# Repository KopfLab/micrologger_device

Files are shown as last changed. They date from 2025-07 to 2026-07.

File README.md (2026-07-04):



# *µLogger*

This repository holds the code, schematics, and documentation to build a ***M**odular **I**nternet **C**ontrollable **R**eal-time **O**ptical-density Logger* (***microLogger*** or ***µLogger*** for short). All content of this repository is free to use for noncommercial research and development efforts as outlined in the terms of the included [LICENSE file](LICENSE.md).

To cite ***µLogger*** in publications use:

> Kopf S and Younkin A, 2025. _µLogger: a Modular Internet Controllable Real-time Optical-density Logger_. <https://github.com/KopfLab/micrologger_device>

A BibTeX entry for LaTeX users is

```
@Manual{
  microLogger,
  title = {µLogger: a Modular Internet Controllable Real-time Optical-density Logger},
  author = {Sebastian Kopf and Adam Younkin},
  year = {2025},
  url = {https://github.com/KopfLab/micrologger_device}
}
```

## About

Modular Internet Controllable Real-time Optical-density Loggers (µLoggers) are optical density measurement devices for continuously recording the growth of a microbial culture directly in its culturing vessel. Each microLogger consists of a compact high strength carbon fibre culture vessel holder that has a built-in light source at a narrow band wavelength and a light sensor with automatically adjustable gain that measures the light transmission across the culture vessel to automatically and continuously quantify optical density at user defined time intervals. A magnetically coupled stirrer built into the vessel holder can agitate the culture both continuously as well as in vortexing mode  (= pulse agitation) at user-set stir/vortexing speeds from 50 to 5000 rpm. Culture vessel adapters that are magnetically secured to the vessel holder allow for quick and easy swapping for differently sized culture vessels and snugly hold the culture vessel in place using a radial spring mechanism. Adapters can be custom sized for the preferred culture vessel from standard 18mm diameter 15mL culture tubes up to 58mm GL45 100mL media bottles. Typical adapter sizes also cover culture vessels typically used in anaerobic microbial culture including balch tubes and serum bottles of varying sizes. Additional optional adapters that are magnetically secured on top of the vessel adapter can provide additional functionality such as user-controlled illumination for experiments with phototrophic microorganisms. Each µLogger is connected to a compact controller (the micrologger "brain") that connects to the culture vessel holder via a single cable such that the vessel holder can be placed inside an incubator (e.g. for temperature or gas modulation) while the controller sits outside the incubator and provides full control and power to the culture vessel holder for stirring, optical density measurements, and (optionally) lighting. The controller has built-in WiFi connectivity and receives/sends data wirelessly wirelessly. This makes it possible to monitor optical density of the microbial cultures in real-time from any location. The controller also has a built-in screen that displays the state of the micrologger (e.g. stir speed, read interval, internet connectivity) as well as the real-time data from the culture vessel so that users can check on their experiments with a glance at the controller without opening the incubator and without handling the culture vessel in any way to avoid potentially disturbing an experiment. For convenience, the controller can also be attached magnetically to the outside of the incubator (if metal) or any other metallic surface.

## Features

- **Continuous optical-density logging** — a narrow-band beam LED and an OPT101 photodetector with automatically optimized amplifier gain measure the light transmission across the culture vessel; the firmware computes optical density (−log₁₀ of transmittance) at user-defined intervals, propagates a standard-deviation error onto every reading, and stores the per-vessel zero reference on the device so it survives power outages.
- **Magnetic stirring & vortexing** — a built-in brushless motor drives a magnetically coupled stirrer with configurable speed, acceleration/deceleration ramps, and a vortex (pulse-agitation) mode; stirring can automatically pause or vortex around each optical-density read.
- **Swappable, magnetically secured vessel adapters** — 3D-printed adapters hold vessels from 18 mm / 15 mL culture tubes up to GL45 100 mL bottles (including Balch/Hungate tubes and serum bottles) with a radial spring mechanism, and accept stacking add-ons such as the illumination adapter.
- **Optional illumination for phototrophs** — a dimmable light adapter with permanent on/off or scheduled (repeating daily-cycle) operation and a light-synced cooling fan.
- **Temperature & power monitoring** — on-board TMP117 temperature sensing at the vessel holder plus supply-voltage monitoring with under-voltage warnings on the display.
- **At-a-glance local display** — the WiFi controller sits outside the incubator, links to the reader over a single cable, and shows live optical density, stir speed, temperature, connectivity, and publishing status on an OLED; it mounts magnetically to any metal surface.
- **Real-time cloud connectivity** — built on the Particle [Photon 2](https://docs.particle.io/reference/datasheets/wi-fi/photon-2-datasheet/); publishes JSON data logs via cloud webhooks (the `microloggerData` event) for recording into spreadsheets or databases, averages data over configurable intervals, and caches logs during offline periods to bridge device downtime.
- **Self-describing & remotely controllable** — the entire device state is exposed as a self-describing data structure (SDDS) that the [sddsParticle](https://github.com/KopfLab/sddsParticle) web GUI (or the Particle CLI/API) can browse and control, with persisted settings, one-shot actions, and per-variable publish intervals.
- **Open & modular** — component-based, easily extensible C++ firmware (separate `sensor`, `stirrer`, `lights`, and `environment` components), open [KiCad](https://www.kicad.org/) hardware, and open [OpenSCAD](https://openscad.org/) 3D-printable mechanical parts.

## Hardware

A µLogger is built from four custom circuit boards, designed in [KiCad](https://www.kicad.org/) with sources under [`pcbs/`](pcbs). For each board the board layout is shown below (click it to open the full schematic / wiring diagram as a PDF).

### Controller board — the µLogger "brain"

A Particle Photon 2 for WiFi and control, the OLED status display, the 24 V power input with supply-voltage monitoring, the controller-version code pins, and the single-cable connector to the reader (the vessel holder).

<a href="pcbs/controller_board/controller_board.pdf">controller board layout</a>

*→ [Controller board wiring diagram (PDF)](pcbs/controller_board/controller_board.pdf)*

### Sensor board

Mounted in the vessel holder: the OPT101 photodiode/transimpedance amplifier with a two-stage digital-potentiometer gain circuit (MCP4017 + AD5246), the TCA9534 I2C IO expander (reader-connection detection plus beam and indicator LEDs), and the measurement-beam LED. The board version is read back over the IO expander.

<a href="pcbs/sensor_board/sensor_board.pdf">sensor board layout</a>

*→ [Sensor board wiring diagram (PDF)](pcbs/sensor_board/sensor_board.pdf)*

### LED board

The optional illumination adapter: the light LEDs driven by a PCA9633 PWM controller for dimming, together with the cooling fan.

<a href="pcbs/led_board/led_board.pdf">LED board layout</a>

*→ [LED board wiring diagram (PDF)](pcbs/led_board/led_board.pdf)*

### Temperature board

A simple TMP117 precision temperature sensor placed at the vessel holder.

*→ [Temperature board wiring diagram (PDF)](pcbs/temperature_board/temperature_board.pdf)*

## 3D printed parts

The vessel holder, stirrer, controller enclosure, and all vessel adapters are 3D-printable. The STL files live in [`prints/stl/`](prints/stl) and the parametric source models are the [OpenSCAD](https://openscad.org/) files [`prints/micrologger_device.scad`](prints/micrologger_device.scad) and [`prints/micrologger_controller.scad`](prints/micrologger_controller.scad). File names ending in `_nozzle_0.4mm` are optimized for a 0.4 mm printer nozzle.

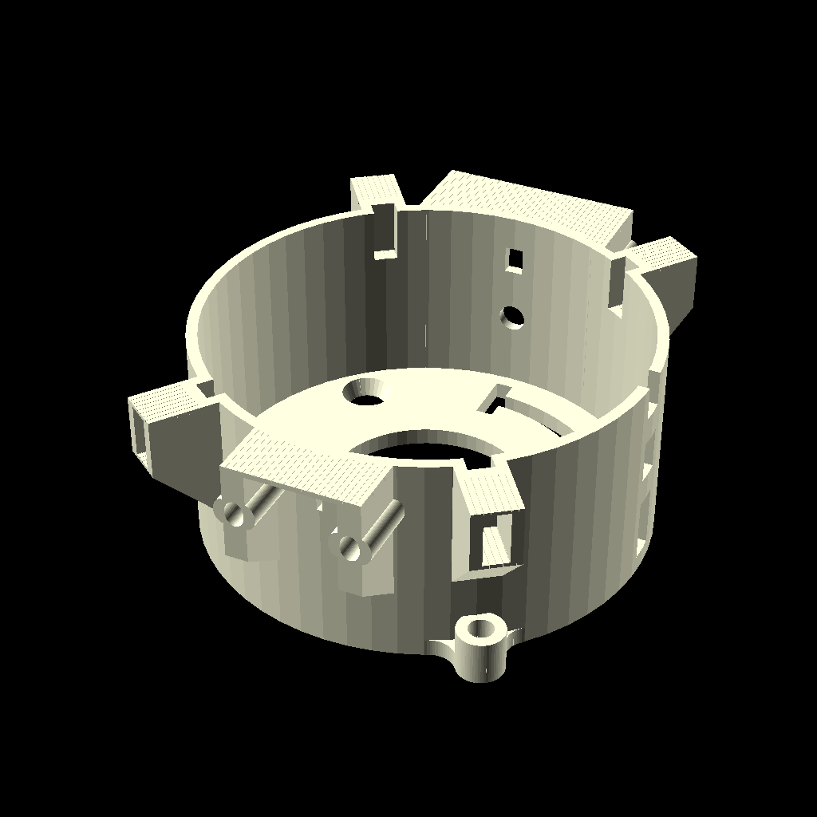
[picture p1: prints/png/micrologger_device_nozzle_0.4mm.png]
µLogger device


The parts fall into a few groups:

- **Device body & stirrer** — the high-strength vessel-holder body (`micrologger_device_*`, designed to be printed in carbon-fibre-reinforced filament) that houses the sensor/beam optics, and the magnetically coupled `micrologger_stirrer_*`.
- **Vessel adapters** — magnetically secured, radially sprung adapters sized for specific culturing vessels: `balch`, `hungate`, `culture60`, `gl45`, `serum60`/`serum120`/`serum160`, plus the `base_*` adapters that go into the base of the vessel holder for small vial sizes.
- **Light adapters** — `micrologger_light_adapter_up`/`_down` for the optional illumination add-on.
- **Controller enclosure** — `micrologger_controller_body`, `micrologger_controller_back`, and `micrologger_controller_magnet_holder` for the "brain" controller box.

👉 See [**`prints/README.md`**](prints/README.md) for the complete list of all printable parts with rendered previews.

## Building, flashing & monitoring

The firmware is written for the Particle Photon 2 (platform `p2`) and built with the [Particle Cloud command line interface (CLI)](https://github.com/spark/particle-cli). Builds are driven by Ruby [Rake](https://ruby.github.io/rake/) (see [`particle_rake.rb`](particle_rake.rb), imported by the [`Rakefile`](Rakefile)) rather than `make`.

First-time setup:

- clone this repository **with submodules** (the `lib/` libraries are git submodules): `git clone --recurse-submodules ...`, or run `git submodule update --init --recursive` in an existing clone
- install the [Particle CLI](https://github.com/spark/particle-cli) and log into your account with `particle login`
- install the ruby gems with `bundle install`

Common Rake shortcuts (run `rake help` for the full list and `rake programs` for the list of compilable programs):

- `rake micrologger` — compile the main firmware in the Particle cloud (`bin/micrologger-p2-<version>-cloud.bin`)
- `rake local micrologger` — compile locally instead (requires the [Particle Workbench](https://docs.particle.io/getting-started/developer-tools/workbench/) local toolchain installed under `~/.particle`)
- `rake dev micrologger` — local compile + flash + watch sources and auto-recompile/-flash on change (via [Guard](Guardfile))
- `rake flash` — flash the newest binary in `bin/` to a USB-connected device (must be in DFU / blinking-yellow mode)
- `rake flash DEVICE=<name>` — flash the newest binary over-the-air via the cloud
- `rake monitor` — open the USB serial monitor
- targets chain, e.g. `rake micrologger flash monitor` compiles, flashes, then monitors

The `tests/` folder holds standalone test programs that build the same way (e.g. `rake blink`, `rake motor`). Which sources/libraries each program compiles is defined in its `.github/workflows/compile-<program>.yaml` file, which drives both local `rake` builds and continuous integration.

## Communicating with the device

The µLogger firmware is built on **self-describing data structures (SDDS)** using the [SDDS library](https://github.com/mLamneck/SDDS) and the [SDDS particleSpike](https://github.com/KopfLab/SDDS_particleSpike). The entire device — every setting, action, and live reading — is exposed as a single SDDS tree (see [The SDDS structure tree](#the-sdds-structure-tree) below).

The primary way to view and control a µLogger is the web-based [sddsParticle](https://github.com/KopfLab/sddsParticle) GUI, which reads a device's structure tree and automatically builds an editor for it. You can also interact with a device directly via the [Particle CLI](https://github.com/spark/particle-cli) (or the equivalent [Particle Cloud API](https://docs.particle.io/reference/api/) requests). All calls require being logged in (`particle login`) and only work for devices registered to your account.

**Reading the tree** (Particle cloud variables):

- `particle get <deviceID> getSddsValues` — the current values of all SDDS variables
- `particle get <deviceID> getSdds` — the full structure tree (types + values)
- `particle get <deviceID> getSddsSystem` — just the `SYSTEM` subtree
- `particle get <deviceID> getSddsCommandLog` — the log of recently received commands

**Setting variables / issuing commands** (Particle cloud function `sdds`): assign values with a `path=value` syntax where the path uses `.` as the separator. Issue several assignments at once by separating them with spaces:

```sh
particle call <deviceID> sdds "sensor.action=zero"
particle call <deviceID> sdds "stirrer.setpoint_rpm=500 stirrer.action=start"
particle call <deviceID> sdds "lights.action=schedule"
```

The return value is `0` when all assignments succeed. For a single failed assignment it is the negated error code (e.g. `-2` when the path could not be resolved); for a batch of assignments it is a bitmask flagging which ones failed. Special codes: `-200` = empty command, `-201` = more than 31 assignments in one call.

**Pushing data to the cloud on demand** (Particle cloud functions): `sendSdds`, `sendSddsValues`, and `sendSddsState` publish the structure tree, all values, or just the saveable state, respectively. Regular data logging is published on the **`microloggerData`** cloud event and configured through the `SYSTEM` structure (see the [SDDS particleSpike documentation](https://github.com/KopfLab/SDDS_particleSpike#the-system-structure)).

## The SDDS structure tree

Every µLogger exposes its complete state as an SDDS tree. Fields can be flagged as _read-only_ (reported by the device but not meant to be edited by the user) or _saveable_ (persisted across restarts, i.e. restored on boot and re-saved with the `SYSTEM` `saveState` action). Numeric fields carry their unit as a name suffix (e.g. `_ms`, `_sec`, `_rpm`, `_V`, `_C`, `_Ohm`, `_percent`, `_ppt` for parts-per-thousand ‰, `_dt` for a date/time, `_HHMM` for a 24h clock time). Actions are one-shot triggers that automatically reset to `___` (no action) after they run.

The top level of the tree contains the `SYSTEM` structure, the `device` connection flag, the four functional components (`sensor`, `stirrer`, `lights`, `environment`), and a low-level `HARDWARE` menu.

### SYSTEM

The `SYSTEM` structure is added automatically by the SDDS particleSpike and carries the device's identity, connection status, health/vitals, persisted-state handling, and all data recording/publishing settings. It is documented in full in the [SDDS particleSpike documentation](https://github.com/KopfLab/SDDS_particleSpike#the-system-structure).

### device

- **`device`** — _read-only_ — whether the controller (the "brain") is connected to the reader (the culture vessel holder) via RJ45 cable: `connected` or `disconnected` (detected via the reader's I2C bus).

### sensor

Optical-density measurement — the core function of the µLogger.

- **`action`** — trigger a one-off measurement action:
  - `zero`: establish the OD = 0 reference for the current culture vessel (typically done once before inoculation). If `gain.automatic` is `yes`, the gain is auto-optimized first, then paused for `gain.zeroPause_ms`, then the zero is recorded. The zero is persisted so it survives power outages.
  - `beamOn`: turn the measurement beam LED permanently on (e.g. to watch the live `reading.saturation_ppt`)
  - `beamOff`: turn the measurement beam off
  - `optimizeGain`: run the automatic amplifier-gain optimization to bring the signal to `gain.target_ppt`
  - `reset`: clear the zero reference and return to idle
- **`status`** — _read-only_ — `idle`, `reading`, `optimizing`, `waiting`, or `zeroing`
- **`reading`** — the latest measurement plus read timing/behavior settings
  - **`saturation_ppt`** — _read-only_ — the current live beam signal as a fraction of the ADC maximum, in ‰; watch this to avoid saturating the detector
  - **`readInterval_ms`** — _saveable_ — how often to take an OD reading (default: 2 minutes)
  - **`vortex`** — _saveable_ — vortex (pulse-agitate) the culture before each read (default: no)
  - **`stopStirrer`** — _saveable_ — stop the stirrer before each read (default: yes)
  - **`stopLights`** — _saveable_ — turn the light off during each read (default: yes)
  - **`wait_ms`** — _saveable_ — settling time after vortex/stirrer stop before reading (default: 0)
  - **`warmup_ms`** — _saveable_ — beam warm-up time whenever the beam turns on (default: 3000)
  - **`cooldown_ms`** — _saveable_ — wait after the beam turns off before reading the dark background (default: 500)
  - **`nextRead`** — _read-only_ — human-readable countdown to the next read
  - **`signal`** / **`signalSd`** — _read-only_ — mean and standard deviation of the beam (lit) signal of the last read
  - **`bgrd`** / **`bgrdSd`** — _read-only_ — mean and standard deviation of the dark-background signal of the last read
  - **`transmittance`** / **`transmittanceSd`** — _read-only_ — light transmittance relative to the zero reference, and its error
  - **`OD`** / **`ODSd`** — _read-only_ — optical density (−log₁₀ of transmittance) and its error
- **`zero`** — the zero reference, persisted so it survives power outages
  - **`last_dt`** — _read-only, saveable_ — timestamp of the last zeroing (`never` if never zeroed)
  - **`valid`** — _read-only, saveable_ — whether a valid zero exists; OD is only computed once this is `yes`
  - **`signal`** / **`signalSd`** — _read-only, saveable_ — beam signal (and SD) recorded at zeroing
  - **`bgrd`** / **`bgrdSd`** — _read-only, saveable_ — dark background (and SD) recorded at zeroing
- **`beam`** — the measurement-beam LED
  - **`status`** — _read-only_ — `on`, `off`, or `error`
  - **`error`** — _read-only_ — I2C error of the beam control
- **`gain`** — the signal amplifier gain
  - **`automatic`** — auto-optimize the gain before zeroing (default: yes; not persisted, so it must be re-enabled each session)
  - **`zeroPause_ms`** — _saveable_ — settling pause after automatic gain optimization before zeroing (default: 60000)
  - **`max_ppt`** — _read-only_ — the maximum attainable signal, in ‰
  - **`target_ppt`** — _saveable_ — target signal level for gain optimization, in ‰ (default: 920)
  - **`gain_Ohm`** — _read-only, saveable_ — the current total amplifier resistance (i.e. the gain), persisted across restarts
  - **`status`** — _read-only_ — `set` or `error`
  - **`error`** — _read-only_ — I2C error of the gain control
- **`error`** — _read-only_ — top-level OD error: `none`, `saturated`, `failedGain`, `failedZero`, or `failedRead`

### stirrer

The magnetically coupled stirrer built into the vessel holder.

- **`action`** — trigger a one-off stirrer action:
  - `start` / `stop`: turn continuous stirring on/off (also updates the persisted `state`)
  - `pause` / `resume`: temporarily stop/restart the motor **without** changing `state` (used internally during reads)
  - `vortex`: run a single vortex pulse — ramp up to `settings.vortexSpeed_rpm`, hold for `settings.vortexTime_sec`, then return to the previous speed
- **`state`** — _read-only, saveable_ — the persisted on/off intent of the stirrer (default: off)
- **`status`** — _read-only_ — `off`, `accelerating`, `decelerating`, `running`, or `error`
- **`error`** — _read-only_ — motor error
- **`event`** — _read-only_ — transient activity: `none`, `paused`, or `vortexing`
- **`setpoint_rpm`** — _saveable_ — target stir speed in rpm (default: 500)
- **`speed_rpm`** — _read-only_ — the measured actual speed in rpm
- **`settings`**
  - **`acceleration_rpm_s`** — _saveable_ — acceleration ramp in rpm per second (default: 500)
  - **`deceleration_rpm_s`** — _saveable_ — deceleration ramp in rpm per second (default: 3000)
  - **`maxSpeed_rpm`** — _saveable_ — maximum allowed speed (capped by the motor hardware limit)
  - **`vortexSpeed_rpm`** — _saveable_ — the speed of a vortex pulse (default: 3000)
  - **`vortexTime_sec`** — _saveable_ — how long to hold at vortex speed (default: 2)

### lights

The optional illumination adapter (for experiments with phototrophic microorganisms) and its cooling fan.

- **`action`** — trigger a one-off light action:
  - `on` / `off`: turn the light permanently on/off
  - `schedule`: run the light on a repeating on/off schedule (see the `schedule*` settings below)
  - `pause` / `resume`: temporarily turn the light off/back on without changing `state` (used during reads when `sensor.reading.stopLights` is yes)
- **`state`** — _read-only, saveable_ — the persisted light mode: `on`, `off`, or `schedule` (default: off)
- **`status`** — _read-only_ — the actual light output: `on`, `off`, or `error`
- **`event`** — _read-only_ — `none` or `paused`
- **`error`** — _read-only_ — I2C error of the light/fan driver
- **`intensity_percent`** — _saveable_ — light brightness, 1–100% (default: 100)
- **`scheduleOn_sec`** — _saveable_ — how long the light stays on per schedule cycle (default: 12 hours)
- **`scheduleOff_sec`** — _saveable_ — how long the light stays off per schedule cycle (default: 12 hours)
- **`scheduleOnStart_HHMM`** — _saveable_ — the time of day the on-phase begins, as a 24h `HHMM` value (default: 1200 = noon)
- **`scheduleInfo`** — _read-only_ — human-readable countdown to the next on/off switch
- **`fan`** — the cooling fan for the light adapter
  - **`action`** — `on`, `off`, or `withLight`
  - **`state`** — _read-only, saveable_ — the persisted fan mode: `on`, `off`, or `withLight` (run the fan only while the light is on) (default: withLight)
  - **`status`** — _read-only_ — `on`, `off`, or `error`

### environment

Temperature and supply-power monitoring.

- **`readInterval_ms`** — _saveable_ — how often to read the temperature sensor (default: 1000)
- **`temperature_C`** — _read-only_ — temperature measured at the vessel holder, in °C
- **`power_V`** — _read-only_ — supply voltage measured at the controller, in V
- **`powerReq_V`** — _saveable_ — the minimum required supply voltage; below this the display warns "not enough power" (default: 20.0)
- **`error`** — _read-only_ — I2C error of the temperature sensor

### HARDWARE

An advanced, low-level menu (added at the end of the tree) that exposes direct access to every peripheral — the I2C IO expander, the digital potentiometers and amplifier gain circuit, the OPT101 light sensor, the TMP117 temperature sensor, the supply-voltage divider, the PCA9633 light/fan PWM driver, the Nidec motor, the OLED display, and the detected controller/sensor PCB versions. It is intended for diagnostics and calibration only; the `sensor`, `stirrer`, `lights`, and `environment` components above are the normal interface.

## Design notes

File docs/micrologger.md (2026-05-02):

# this is basically the ministat v2

# sensor - OPT101

## power

- can run at any voltage from 2.7 to 36V and output is **indepenent** of the input voltage but will max out ~1V below the power and no longer record higher light intensities
- to max out GPIO input (3.3V), need to drive at > 4V (5V works well) but then need to also protect the GPIO input against overvoltage which gets problematic at ~3.7 V
- to protect this, use a small signal schottky diode with low forward voltage drop (ideally ~200mV) to the 3.3V supply to clamp the voltage on the GPIO pin to 3.3V + 0.2V = ~ 3.5 V, options:
    - BAT41: at 1mA max drop is 450mV (looks like ~250mV at 0.1mA) and very low leakage current (only 100 nA at 50V) --> seems to have the lowest leak A and V drop for through hole components
    - BAT43W (SMD only): at 2mA max drop is 330mV, 450mV at 15mA
    - BAT54 (SMD only): at 0.1mA max drop is 240mV, 1mA max drop is 320mV (very similar to 43W)
    - BAT81, 82, 83: at 0.1mA max drop is 330 mV    
    - some other options: https://www.vishay.com/en/diodes/ss-schottky/

## I2C addresses:

 - MCP4652 (dual trimpot): 0x2C if address pins tied to ground
 - MCP5241 (single trimpot): 0x2C if address pins tied to ground
 - I2C display: 0x3c
 - IR temperature sensor: 0x5a
 - tmp117 temperature sensor: 0x48
 - TCA9534 gpio expander: 0x20 --> https://learn.sparkfun.com/tutorials/sparkfun-qwiic-gpio-hookup-guide#arduino-examples
 - PWM controller PCA9633: 0x62 for inidviual, 0x70 for AllCall address (to all PCA9633 chips), and 0x03 for software reset. This chips is a 4-bit, 4 channel fan (mosfet), light sheet (mosfet)
 - not used MCP4017: 0x2f --> https://github.com/SparkysWidgets/SW_MCP4017-Library
 - not used AD5246: 0x2e --> https://github.com/SparkysWidgets/SW_MCP4017-Library

## signal

- typically need to reduce the signal amplification with resistors < 1MOhm
- with LED driven at ~3.3V from a GPIO pin, a ~250 kOhm resistor usually maxes out the detector to its reference voltage even if it's as high as 24V
- the current is typically low, even at full intensity with a high resistor value (and corresponding signal voltage), this stays < 10µA (but will rise rapidly if it exceeds the internal GPIO overvoltage of ~3.7V) - for stability best to stay at max overvolage of 3.4V (not all the way to 3.7!), this can be reached with a supply voltage of 4.2V to the OPT100 and light saturation --> a voltage divider with 1kOhm and 6.8kOhm will lead to voltage of ~4.2V (starting with 5V supply, note that voltage divider predicts slightly higher but we have some pulls to GND that lower this slightly) which should work for this. Current draw of the opt can be up to 4mA current to OPT101 (and ~0.7mA dead current from source to sink)
- if signal instability is an issue, can place a 0.01-μF to 0.1-μF (e.g. 67 pF) bypass capacitor close to sensor to connect Vin & Gnd. Additionally for low resistanece (i.e. low amplification) at or below 100 kOhm, might also need a capacitor (33 pF for 100kOhm, higher for others) across the resistor
- pulldown resistor to signal line should be 10 kOhm or bigger (no need to have them lower since the voltage is clamped to ~3.7V), use 47 kOhm or even 100 kOhm as a more common pulldown! Note that using an external resistor is a bit more reliable than internal (digital) pulldowns which are different on different pins and from controller to controller - this resistor could be surface mounted
- a digital trimmer could provide programmatic control over the amplification, try out AD5241 (1 trimmer with 2 additional logic outputs), which could also logic control 2 other things via the I2C (e.g. motor on/off, and with a MOSFET the LED on/off) --> since the AD5241 runs 5V logic, need to use a level shifter for Argons/P2s, simplest is this tiny Pololu PCB with mosfets (https://www.pololu.com/product/2595) or slightly bigger Sparkfun PCB with BSS138 mosfets (probably works too with BS270): https://cdn.sparkfun.com/datasheets/BreakoutBoards/Logic_Level_Bidirectional.pdf - alternatively just make the level shifting circuits yourself on the controller PCB

# amplification / digital potentiometer

need to be able to cover a range of ~200 kOhm but the most commonly available are 100 kOhm (1 MOhm could work too but then the gain adjustment is too course), this is achieved most easily by a either a dual 100kΩ rheostat or two separate 100kΩ rheostats

## 1 dual rheostat

 - MCP4652 100kΩ Dual Rheostat, tempco 50 ppm/C, 8-bit (256 steps): https://jlcpcb.com/partdetail/MicrochipTech-MCP4652T_104EMF/C623638
 - alternative (with 2 extra pins): MCP4651 100kΩ Dual Potentiometer version of MCP4652 https://jlcpcb.com/partdetail/MicrochipTech-MCP4651_104EST/C637129
 - AD5248 is the equivalent to MCP4652 (8-bit 100kΩ Dual Rheostat) but only 35 ppm/C tempco, also a lot more expensive and not as available: https://jlcpcb.com/partdetail/AnalogDevices-AD5248BRMZ100/C144252, this might be useful for programming: https://learn.adafruit.com/ds3502-i2c-potentiometer/overview

## 2 single rheostats

 - AD5246 100kΩ Single Rheostat, tempco 45ppm/C, 4-bit (128 steps): https://jlcpcb.com/partdetail/AnalogDevices-AD5246BKSZ100RL7/C649406
 - MCP4017 100kΩ Single Rheostat, tempco 50ppm/C, 4-bit (128 steps): https://jlcpcb.com/partdetail/MicrochipTech-MCP4017T_104ELT/C510890 (discontinued)
 - newer version: MCP40D17 (same specs as MCP4017): https://jlcpcb.com/partdetail/MicrochipTech-MCP40D17T_104ELT/C115214 (not available yet)
 - MCP4532 100kΩ Single Potentiometer, tempco 50ppm/C, 4-bit (128 steps): https://jlcpcb.com/partdetail/MicrochipTech-MCP4532T_104EMS/C627275

# LED - 630nm (MTE7063NK2)

 - this LED has 50mA max current but best to drive at 20-30mA where it has ~1.9 V forward voltage
 - with 47 Ohm resistor and 3.3V supply this runs at ~30mA
 - with 100 Ohm resistor and 5V supply this runs at ~31mA  
 - can drive the LED from the AD5241 extra logic output with a BS170 or BS270 (lower gate voltage?) mosfet (or the equivalent SMD component) --> keep in mind that as diodes these have forward voltage drops that will aslo affect the LED current! need to test this out but it should only be a few mV

# temperature sensing

 - use a temp sensor via I2C since that's already going to the micrologger now
 - ideally use tmp117 (https://cdn.sparkfun.com/assets/2/0/f/c/a/SparkFun_TMP117_Qwiic_Schematic_v1.pdf, address 0x48) but I don't see a good packaged version yet, alternatively the tmp100? another interesting option is a low angle (10degree) IR temperature sensor, such as this one: https://www.digikey.com/en/products/detail/melexis-technologies-nv/MLX90614ESF-ACF-000-TU/2652200 that can communicate via I2C like protocol, this one could go right underneat the light sensor on the same PCB and going through the wall of the micrologger (it's okay if it records IR from the stir bar + liquid) - for notes on how to get started with communication, check out this testing board: https://www.sparkfun.com/products/10740

# display

 - switching to oled: https://www.youtube.com/watch?v=7x1P80X1V3E with this model (which is easily available from various amazon vendors for about $14): https://www.amazon.com/gp/product/B09LND6QJ1
 - needs to be switched from SPI to I2C
 - great resource: https://luma-oled.readthedocs.io/en/latest/hardware.html
 - great summary of the different resistors: https://www.amazon.com/gp/customer-reviews/R373WMLIYUB5MF/ref=cm_cr_dp_d_rvw_ttl?ie=UTF8&ASIN=B09LND6QJ1
 - attach to PCB with M2.5 x 28mm threaded spacers from Mouser (761-M1273-2545-AL) and with narrow head M2.5 x 6mm machine screws from McMaster (cheaper: 91800A126 or nicer: 94017A152)
 - don't want to have it on the 3.3V so we don't have any interference but also a problem if it's on the 5V when the 5V rail is competing between the USB and DC/DC adapter

# lights

 - Auragami light sheets need 24V power and are 26mW (~1.1 mA at 24V) per LED --> with 40 LEDs this should only be about 50mA

# motor

 - Nidec 24H brushless servo motor requires 22.8 to 25.2V to power. No-load current at 24V (5200 to 6400rpm) is about 110mA, max power is 11W (~460mA)
    -> pin 8/red: power (+24VDC)
    -> pin 7/black: ground (GND)
    -> pin 6/yellow: speed (as long as break is not engaged), freq 20 to 30 kHz (25000 works welll), duty cycle = speed (0 = stop, 255 = max speed)
      note: LED dimmers like the PCA9633 we're using cannot operate at this frequency, the simplest solution if we do not want to use a line on the RJ45 for motor speed is to use a small microcontroller (e.g. ATtiny402) on the sensor board side that talks to the photon by I2C and takes care of the PWM for the motor, the LED on/off and the light control
    -> pin 5/green: break, HIGH = engaged (stop), LOW = not engaged (pin 6 decides speed) --> set permanently to LOW
    -> pin 4/blue: direction, HIGH (2 to 5V) = CW, LOW = CC --> set permanently to one or the other (jumper selectable?)
    -> pin 3/white: power for the decoder, can be 5 VDC or 3.3 VDC --> pin 7/8 signals are this voltage use 3.3 VDC OR use a level shifter (can use multiple channel ones, one for the I2C, one for this?)
    -> pin 2/orange: signal of the optical decoder, seems like it has 100 pulses per revolution so freq (in Hz) / 100 * 60 = rpm
    -> pin 1/brown: offset (falling edge) of the decoder, same info as pin 2 if we already know cc vs cw
        - 0/255: stop
        - 1/255: doesn't work
        - 2/255: 37 Hz ~ 22 rpm
        - 3/255: 78 Hz ~ 47 rpm
        - 4/255: 116 Hz ~ 70 rpm
        - 5/255: 153 Hz ~ 92 rpm
        - 10/255: 330 Hz ~ 198 rpm
        - 20/255: 694 Hz ~ 416 rpm
        - 50/255: 1.6 kHz ~ 960 rpm ~ 50 mA without load
        - 100/255: 3.1 kHz ~ 1860 rpm ~ 140 mA without load
        - 150/255: 4.9 kHZ ~ 2900 rpm ~ 170 mA without load
        - 255/255: 9.54 kHz ~ 5700 rpm ~ 70 mA without load (current max without load actually seems to be around 150/255)
        --> estimated formula for 8 bit: x/255 --> rpm = (x-1) * 22 rpm (response factor more like 20rpm around 150/255 and then goes back to 22 rpm again)
        --> for 12 bit:
        --> x = (rpm/22 + 1) * 16 = 16 + rpm * 16/22
        - with interrupt delays of about 40-70uS we should be able to measure the entire range (10 kHz = 100µs interrupts) but I'm not sure if anything else will mess with that during operation

## motor power

 - the speed pin (6/yellow) needs to be pulled low to GND otherwise the motor spins on start-up (unless break is engaged which can cause other problems)
    --> if pulled low with 1kOhm resistor the voltage is about 0.44V (see analysis below) which suggests the motor has an internal pullup on this pin to 5V of about ~10 kOhm
    --> if controlling this with a mosfet, need to provide an alternative path to high voltage that pulls the voltage above ~0.7V (also considering the body diode voltage drop of the moseft, ~0.8V at most)
    --> see circuit analysis
 - resistor values for pull down to ground (assumes ON = direct connection to 5V):
    - 2.3kOhm: pull down does NOT work because effective voltage on the pin is 1.34V (counts as HIGH), 0.35 mA to GND
    - 2.2k: 0.845 V, 0.4 mA to GND when off, 2.2mA to GND when on
    - 1.5k: 0.597 V, 0.42 mA to GND when off, 3.34mA to GND when on (2mA if 3.3V supply voltage)
    - 1k: 0V, 0.44 mA to GND when off, 5mA to GND when on (3mA if 3.3V supply voltage)
 --> with a BSS138 use a 1000 Ohm resistor to pull to ground (with the 10kOhm pull up internally to 5V, this gives a voltage of 0.44V which is low enough to deactivate the motor and only a 0.5mA standby current)
 --> then the mosfet shifts it with a parallel resistor to 5V that is 1kOhm which makes the net resistor 900 Ohm and pulls the voltage to ~2.5V which is enough to activate motor and a total of ~2.6 mA current which is totally fine
 --> I modeled this in a circuit lab circuit (but don't have good access)
 Note that this circuit is divided between the sensor board (with the pulldown to GND to have it off by default), and the brain where the I/O step up from 3.3 V to 5V is located (unidirectional level shifter if you will) mostly beccause space is abundant on this end but really limited on the sensor board but in theory this could all be sitting on the sensor board side

## motor attachment

corner standoffs for micrologger base
- base is 34 mm high
- rotor is 20 mm above base
- magnet holder is at least 3.5 mm tall (3.2 mm magnets plus 0.25mm base layer)
- i.e. total is 57.5mm
- with the longest metric standoffs from McMaster (52mm long, 95947A087) this requires a rather thick base (>5.5mm) so need to go with an imperial standoff: 2.25" is 57.15mm long (93505A006) which is male/female and thus can just thread directly into the nylon base

mounting standoffs for motor itself
- base plus mounting bracket is 3.5 mm above the motor base so 20mm shaft + 3.5 mm magnet holder - 3.5mm bracket height  - 4mm µlogger base thickness = 16mm M4 standoffs (McMaster, 95947A050). For a little extra clearance might have to make the base 5mm thick!
- plus 6mm round head M4 screws (92000A216) to attach from motor side, and 10mm flat head M4 screws (92010A220) to attach through µLogger base

## motor magnets
- 3.2 mm above the motor shaft, design/print upside down with a thin layer (0.25 mm) base then the magnet holes above (unroofed since the top of the motor assembly will hold them in place) and then the side walls above where there is solid support underneath to grip the motor shaft with the teeth walls --> total is ~3.5 mmm above the motor shaft so total then becomes 54mm + 3.5mm = 57.5mm which requires a rather thick base (~5.5mm to still work with the 52mm feet)
-  

# overall power

power over ethernet technical specs (up to 100m distance): https://www.blackbox.com/en-nz/insights/blogs/detail/technology/2021/05/04/poe-cabling-what-you-need-to-know-part-1
 - PoE+	IEEE 802.3at (Type-2)	25.5 W	30 W	2-pair	0.6 A	PTZ cameras, video IP phones, alarm systems
 - PoE++ IEEE 802.3bt (Type 4)	71.3 W	100 W	4-pair	0.96 A	PoE-Powered LED Lighting, outdoor PTZ cameras

but technical specs:
    Maximum Current Carrying Capacity of Ribbon Cable (while keeping temperature rise to less than 30 °C)
    24 AWG	3.0 A
    26 AWG	1.8 A
    28 AWG	1.5 A
    30 AWG	1.1 A

# power supply voltage

 - R1: 10kOhm = 9.93
 - R2: 200kOhm = 200.1

forward voltage drop across the M400x diode is 0.6 V with minimal current and ~0.9 V at 1A (probably best to calculate with assumed 0.9V drop)

sensing calculation:
V at A0 = Vin * R1/(R1+R2) --> Vin = A0 * (10 + 200)/10 + 0.9V

 External voltage sensing on P2 pin A0:
  - R1 = 150 kOhm, R2 = 10 kOhm
  --> V at A0 for 24V --> 24V * 10/(10+150) = 1.5External voltage sensing on P2 pin A0:
   - R1 = 150 kOhm, R2 = 10 kOhm
   --> V at A0 for 24V --> 24V * 10/(10+150) = 1.550

# ethernet cable

 - 8p8c: 1=Gnd, 2=24V, 3=I2C-SDA, 4=I2C-SCL, 5=Motor-speed, 6=Detector-signal, 7=Light-intensity, 8=Motor-decoder
 -> 24V to 5V required on distribution board; level shifters required to convert 5V from I2C and motor-decoder

# connectors

 - the JST XHP connectors (2.54mm) are used by the light sheets and are easy to buy from amazon, including different length cables that can be easily assembled
 - the JST PH (2.0mm) connectors are primarly used to connect batteries (e.g poli) and usually are male to female connectors
 - the JST ZH connectors (1.5mm, 26 AWG, 1.0 A rating), are used by the motor connectors / JST ZR connectors are compatible but lower amperage rating (0.7A, 28 AWG)

# housing
 - threaded spacers between OLED and main PCB are M2.5, 28mm long: https://www.mouser.com/ProductDetail/761-M1273-2545-AL
 - standoff spacers between main PCB and back wall are M3, 12mm long (this length does not seem to be available for M2.5): https://www.mcmaster.com/94669A307/

# checklist

 - power up with 24V / GND pins (not via ethernet!)
 - when powered up but beam OFF:
    - signal vs. gain resistance should be ~200kOhm (100 kOhm base resistor + 2 * 50 kOhm = midpoints of the digipots), doesn't matter if motor and/or light are also on
    - when a little bit of light is shining on the detector, the resistance should go up (with much light into several MOhm and too high to measure)
    - signal vs. ground voltage should be < 20mV, when detector opening completely covered ~ 10mV (this is a bit higher with motor and/or lights on and/or beam on but detector covered up)
    - when a little bit of light is shining on the detector, the voltage should go up
 - when powered up and beam ON:
    - signal vs gain restiance should be immesurably high (unless detector is covered in which case it should be back to ~200 kOhm)
    - signal vs ground voltage should be at ~3.2 V
 - plugging in the ethernet cable should only have minimal effects (both loose cable and connector to empty/microcontroller less brain)
 - neither should switching to brain powersupply have any effect

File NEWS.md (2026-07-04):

NB:
 - version updates at the 0.x level usually require a state reset because they change/add/remove state variables, i.e. should never be done in the middle of an experiment. 
 - version changes at the 0.0.x level can be flashed at any time. They do make state changes and thus will resume their current state correctly after flash+restart.

# version 1.5.1

- publish on the `microloggerData` event instead of `sddsData` for microloggers
- rename `publishing.publish` to `publishing.record` to clarify how it relates to GUI recording on/off
- hardware `signal.calculation` added with two possible values: `mean` (default, average signal values) or `mode` (determine peak of the signal values)
- optical density `reading.stopLights` added for users to decide whether lights turn off or stay on during OD reads (default is stopLights = yes)
- system `state.autoSendOnStartup` added for users to decide whether to send the state snapshot whenenver a device that's recording starts up (e.g. after power cycling), default is ON
- introduce particle variable `getSddsSystem` as convenience access piont that returns the system variable tree only (~800 bytes in size) except for the variable publish intervals (which can be any size)
- change default read interavl to 2 min and default publish interval to 20 min

# version 1.4.0

- `cooldown` (wait time until dark measurement after LED beam turned off, default: 500 ms) added - this value is saved in the micrologger state
- `zeroPause` (wait time until zeroing when automatic gain adjustment happens during zeroing, default: 60s) introduced - this value is saved in the micrologger state
- default values for `warmup` (default: 3s) and `wait` (default: 0s) adjusted since the longer warmup leads to a more stable signal but usually does not require additional wait time anymore for the culture to settle

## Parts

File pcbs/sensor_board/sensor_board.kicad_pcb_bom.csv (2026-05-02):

Designator | Quantity | Value | Footprint | Package | MPN | DNP | Mount_Type | Description | JLCPCB | JLCPCBURL | DigiKey | DigiKeyURL
C1 | 1 | 100pF | C_0603 |  |  |  | smt | Unpolarized capacitor | C14858 | https://jlcpcb.com/partdetail/15530-CL10C101JB8NNNC/C14858
C2, C3, C4, C5 | 4 | 100nF | C_0603 |  |  |  | smt | Unpolarized capacitor | C1591 | https://jlcpcb.com/partdetail/1943-CL10B104KB8NNNC/C1591
D1 | 1 | Red 631nm 2.0V | LED_1206 |  | LTST-C150KRKT |  | smt | Red 631nm LED Indication - Discrete 2V 1206 (3216 Metric) | C125086 | https://jlcpcb.com/partdetail/LiteOn-LTSTC150KRKT/C125086 | 160-1405-1-ND | https://www.digikey.com/en/products/detail/liteon/LTST-C150KRKT/386761
D2 | 1 | Yellow 571nm 2.0V | LED_1206 |  | LTST-C150KGKT |  | smt | Green 571nm LED Indication - Discrete 2V 1206 (3216 Metric) | C125085 | https://jlcpcb.com/partdetail/LiteOn-LTSTC150KGKT/C125085 | 160-1404-1-ND | https://www.digikey.com/en/products/detail/liteon/LTST-C150KGKT/365085
D3 | 1 | 1A/40V/500mV | D_DO-214AC_SMA |  | SS14 |  | smt | Diode 40 V 1A Surface Mount DO-214AC (SMA) | C83852 | https://jlcpcb.com/partdetail/onsemi-SS14/C83852 | SS14CT-ND | https://www.digikey.com/en/products/detail/onsemi/SS14/965474
J1 | 1 | 1.5mm | JST_ZH_2POS_RA |  | S2B-ZR |  | tht | Connector Header Through Hole, Right Angle 2 position 0.059" (1.50mm) |  |  | 455-1669-ND | https://www.digikey.com/en/products/detail/jst-sales-america-inc/S2B-ZR/926576
J2, J3 | 2 | 2.5mm | JST_XH_2POS_RA |  | S2B-XH-A |  | tht | Connector Header Through Hole, Right Angle 2 position 0.098" (2.50mm) |  |  | 455-S2B-XH-A-ND | https://www.digikey.com/en/products/detail/jst-sales-america-inc/S2B-XH-A/1651055
J4 | 1 | 1.5 mm | JST_ZR_8POS_RA |  | S8B-ZR |  | tht | Connector Header Through Hole, Right Angle 8 position 0.059" (1.50mm) |  |  | 455-S8B-ZR-ND | https://www.digikey.com/en/products/detail/jst-sales-america-inc/S8B-ZR/926582
J5 | 1 | RJ45 | RJ45_A-2014-2-4-N-T-R |  | A-2014-2-4-N-T-R |  | tht | Jack Modular Connector 8p8c (RJ45, Ethernet) Vertical Unshielded |  |  | AE10396-ND | https://www.digikey.com/en/products/detail/assmann-wsw-components/A-2014-2-4-N-T-R/2183647
J6 | 1 | Conn_01x06 | PIN_HEADERS_1X06 |  |  |  | tht | Basic 0.1" PTH
J7, J8 | 2 | Conn_01x02 | PIN_HEADERS_1X02 |  |  |  | tht | Basic 0.1" PTH
JP1, JP2, JP3, JP4 | 4 | ~ | Jumper_3_NC-1_Trace |  |  |  | tht | 3-pole Solder Jumper, pins 1+2 closed/bridged
Q1, Q2, Q3 | 3 | 220mA / 50V | SOT-23-3 |  | BSS138 |  | tht | N-Channel 50 V 2200mA 350mW (Ta) Surface Mount SOT-23-3 | C52895 | https://jlcpcb.com/partdetail/onsemi-BSS138/C52895 | BSS138CT-ND | https://www.digikey.com/en/products/detail/onsemi/BSS138/244210
R1, R11, R3, R5 | 4 | 1kΩ | R_0603 |  |  |  | smt | Resistor, US symbol | C118155 | https://jlcpcb.com/partdetail/PANASONIC-ERJ3EKF1001V/C118155
R10, R15, R9 | 3 | 150Ω | R_0603 |  |  |  | smt | Resistor, US symbol | C400650 | https://jlcpcb.com/partdetail/PANASONIC-ERJ3EKF1500V/C400650
R12, R13, R14, R16, R2, R7, R8 | 7 | 10kΩ | R_0603 |  |  |  | smt | Resistor, US symbol | C191124 | https://jlcpcb.com/partdetail/PANASONIC-ERJ3EKF1002V/C191124?_t=1765754579496
R4 | 1 | 10kΩ | R_1206 |  |  |  | smt | Resistor, US symbol | C17902 | https://jlcpcb.com/partdetail/18590-1206W4F1002T5E/C17902
R6 | 1 | 5.6kΩ | R_0603 |  |  |  | smt | Resistor, US symbol | C403276 | https://jlcpcb.com/partdetail/PANASONIC-ERJ3EKF5601V/C403276
S1 | 1 | Value | OPT101 |  | OPT101 |  | tht | Optical Sensor Ambient 650nm Voltage 8-DIP (0.300", 7.62mm) |  |  | 296-23090-5-ND | https://www.digikey.com/en/products/detail/texas-instruments/OPT101P/251177
S2 | 1 | IR temp sensor, -40°C to +85°C | MLX90614 |  | MLX90614ESF-ACC-000-TU |  | tht | Temperature Sensor Digital, Infrared (IR) -40°C ~ 85°C 16 b TO-39, 5V |  |  | MLX90614ESF-ACC-000-TU-ND | https://www.digikey.com/en/products/detail/melexis-technologies-nv/MLX90614ESF-ACC-000-TU/1948826
U1 | 1 | 8-28V in / 5V 5W out | DC_DC_converter_R-78E5.0-1.0 |  | R-78E5.0-1.0 |  | tht | Linear Regulator Replacement DC DC Converter 1 Output 5V 1A 8V - 28V Input |  |  | 945-2201-ND | https://www.digikey.com/en/products/detail/recom-power/R-78E5-0-1-0/4930585
U2 | 1 | 8x GPIO | SOT-403-1_TSSOP16 |  | TCA9534PWR |  | tht | I/O Expander 8 I2C 400 kHz 16-TSSOP | C783615 | https://jlcpcb.com/partdetail/TexasInstruments-TCA9534PWR/C783615 | 296-40574-1-ND | https://www.digikey.com/en/products/detail/texas-instruments/TCA9534PWR/5004966
U3 | 1 | 4x PWM | SOT-505-1_TSSOP8 |  | PCA9633DP1,118 |  | smt | LED Driver IC 4 Output Power Switch I2C Dimming 25mA 8-TSSOP | C88381 | https://jlcpcb.com/partdetail/NXPSemicon-PCA9633DP1118/C88381?_t=1765688339929 | 568-3236-1-ND | https://www.digikey.com/en/products/detail/nxp-usa-inc/PCA9633DP1-118/1033521
U4 | 1 | 1 MOhm | 14-SOIC |  | AD5241BRZ1M |  | smt | Digital Potentiometer 1M Ohm 1 Circuit 256 Taps I2C Interface 14-SOIC | C649389 | https://jlcpcb.com/partdetail/AnalogDevices-AD5241BRZ1M/C649389 | 505-AD5241BRZ1M-ND | https://www.digikey.com/en/products/detail/analog-devices-inc/AD5241BRZ1M/617299
U5 | 1 | 100 kOhm | SOT-363_TSSOP6_SC88 |  | MCP4017T-104E/LTY |  | smt | Digital Potentiometer 100k Ohm 1 Circuit 128 Taps I2C Interface SC-70-6 | C510890 | https://jlcpcb.com/partdetail/MicrochipTech-MCP4017T_104ELT/C510890 | 150-MCP4017T-104E/LTYCT-ND | https://www.digikey.com/en/products/detail/microchip-technology/MCP4017T-104E-LTY/26812128

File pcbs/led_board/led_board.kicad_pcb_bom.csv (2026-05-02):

Designator | Quantity | Value | Footprint | Package | MPN | DNP | Mount_Type | Description | DigiKey | DigiKeyURL | Sim.Pins | URL | JLCPCB | JLCPCBURL | FP_Status
J1 | 1 | CONN HEADER R/A 2POS 1.5MM | JST_ZH_2POS_RA |  | S2B-ZR |  | tht | Connector Header Through Hole, Right Angle 2 position 0.059" (1.50mm) | 455-1669-ND | https://www.digikey.com/en/products/detail/jst-sales-america-inc/S2B-ZR/926576
LED1 | 1 | 630nm 1.9V 50mA | TO-46-2 |  | MTE7063NK2-UR |  | tht | Visible Emitter 630nm 1.9V 50mA 5° TO-46-2 Lens Top Metal Can | 1125-1382-ND | https://www.digikey.com/en/products/detail/marktech-optoelectronics/MTE7063NK2-UR/6817919 | 1=K 2=A | https://www.digikey.com/en/products/detail/marktech-optoelectronics/MTE7063NK2-UR/6817919
R1 | 1 | 22Ω | R_1206 |  |  |  | smt | Resistor, US symbol |  |  |  |  | C17958 | https://jlcpcb.com/partdetail/18646-1206W4F220JT5E/C17958
R2 | 1 | 56Ω | R_1206 |  |  |  | smt | Resistor, US symbol |  |  |  |  | C17995 | https://jlcpcb.com/partdetail/18683-1206W4F560JT5E/C17995 | done
U1 | 1 | 1.4-40V PWM Dimmer 100mA | SOT-23-6 |  | BCR401UW6Q-7 |  | tht | LED Driver IC 1 Output Linear PWM Dimming 100mA SOT-26 | BCR401UW6Q-7DICT-ND | https://www.digikey.com/en/products/detail/diodes-incorporated/BCR401UW6Q-7/7352843 |  | https://www.digikey.com/en/products/detail/diodes-incorporated/BCR401UW6Q-7/7352843 | C2678813 | https://jlcpcb.com/partdetail/DiodesIncorporated-BCR401UW6Q7/C2678813

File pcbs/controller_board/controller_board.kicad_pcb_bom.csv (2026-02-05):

Designator | Quantity | Value | Footprint | Package | MPN | DNP | Mount_Type | Description | JLCPCB | JLCPCBURL | FP_Status | DigiKey | DigiKeyURL | UnitPrice | ParticleURL
C1 | 1 | 10nF | C_0603 |  |  |  | smt | Unpolarized capacitor | C1589 | https://jlcpcb.com/partdetail/1941-CL10B103KB8NNNC/C1589
D1 | 1 | 3A/60V/750mV | D_DO-214AB_SMC |  | SS36 |  | tht | Diode 60 V 3A Surface Mount DO-214AB (SMC) | C391251 | https://jlcpcb.com/partdetail/onsemi-SS36/C391251 | done | SS36FSCT-ND | https://www.digikey.com/en/products/detail/onsemi/SS36/1053019
D2 | 1 | 1A/40V/500mV | D_DO-214AC_SMA |  | SS14 |  | smt | Diode 40 V 1A Surface Mount DO-214AC (SMA) | C83852 | https://jlcpcb.com/partdetail/onsemi-SS14/C83852 | done | SS14CT-ND | https://www.digikey.com/en/products/detail/onsemi/SS14/965474
D3 | 1 | 40V | D_DO-214AA_SMB |  | SMBJ36A |  | tht | 58.1V Clamp 10.4A Ipp Tvs Diode Surface Mount DO-214AA (SMBJ) | C224020 | https://jlcpcb.com/partdetail/Littelfuse-SMBJ36A/C224020 | done | SMBJ36ALFCT-ND | https://www.digikey.com/en/products/detail/littelfuse-inc/SMBJ36A/286010
F1 | 1 | 33V/750mA/1.5A | Fuse_1812 |  | MF-MSMF075/33X-2 |  | smt | Polymeric PTC Resettable Fuse 33V 750 mA Ih Surface Mount 1812 | C3760814 | https://jlcpcb.com/partdetail/BOURNS-MF_MSMF075_33X2/C3760814 | done | 118-MF-MSMF075/33X-2CT-ND | https://www.digikey.com/en/products/detail/bourns-inc/MF-MSMF075-33X-2/16357034 | 0.91
J1 | 1 | RJ45 | RJ45_A-2014-2-4-N-T-R |  | A-2014-2-4-N-T-R |  | tht | Jack Modular Connector 8p8c (RJ45, Ethernet) Vertical Unshielded |  |  | done | AE10396-ND | https://www.digikey.com/en/products/detail/assmann-wsw-components/A-2014-2-4-N-T-R/2183647
J2 | 1 | Conn_01x07 | PIN_HEADERS_1X07 |  |  |  | tht | Basic 0.1" PTH |  |  | done
J3 | 1 | Conn_01x12 | PIN_HEADERS_1X12 |  |  |  | tht | Basic 0.1" PTH |  |  | done
J4 | 1 | PINHD-1X4 | PIN_HEADERS_1X04 |  |  |  | tht | Basic 0.1" PTH |  |  | done
P1 | 1 | 24V / 5A | PWR_JACK_PJ-064A |  | PJ-064A |  | tht | 2.0 mm Center Pin, 5.0 A, Vertical, Panel Mount, PC Pins, Dc Power Jack Connector |  |  | done | CP-064A-ND | https://www.digikey.com/en/products/detail/cui-devices/PJ-064A/2627221
Q1, Q2, Q3, Q4 | 4 | 220mA / 50V | SOT-23-3 |  | BSS138 |  | tht | N-Channel 50 V 2200mA 350mW (Ta) Surface Mount SOT-23-3 | C52895 | https://jlcpcb.com/partdetail/onsemi-BSS138/C52895 | done | BSS138CT-ND | https://www.digikey.com/en/products/detail/onsemi/BSS138/244210
R1 | 1 | 150kΩ | R_1206 |  |  |  | smt | Resistor, US symbol | C17916 | https://jlcpcb.com/partdetail/18604-1206W4F1503T5E/C17916 | done
R10, R11, R12, R13, R14, R16, R17, R18, R2, R5, R7, R9 | 12 | 10kΩ | R_1206 |  |  |  | smt | Resistor, US symbol | C17902 | https://jlcpcb.com/partdetail/18590-1206W4F1002T5E/C17902 | done
R3 | 1 | 100kΩ | R_1206 |  |  |  | smt | Resistor, US symbol | C17900 | https://jlcpcb.com/partdetail/18588-1206W4F1003T5E/C17900 | done
R4, R8 | 2 | 1kΩ | R_1206 |  |  |  | smt | Resistor, US symbol | C4410 | https://jlcpcb.com/partdetail/4817-1206W4F1001T5E/C4410 | done
R6 | 1 | 150Ω | R_1206 |  |  |  | smt | Resistor, US symbol | C17917 | https://jlcpcb.com/partdetail/18605-1206W4F1500T5E/C17917 | done
U1 | 1 | 8-28V in / 5V 5W out | DC_DC_converter_R-78E5.0-1.0 |  | R-78E5.0-1.0 |  | tht | Linear Regulator Replacement DC DC Converter 1 Output 5V 1A 8V - 28V Input |  |  | done | 945-2201-ND | https://www.digikey.com/en/products/detail/recom-power/R-78E5-0-1-0/4930585
U2 | 1 | Particle2 / Boron | PHOTON2 |  | PHN2MEA / BRN404 |  | tht | Particle Photon 2 Wi-Fi enabled development kit |  |  | done |  |  |  | https://store.particle.io/collections/wifi/products/photon-2

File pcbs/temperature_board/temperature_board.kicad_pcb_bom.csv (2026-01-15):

Designator | Quantity | Value | Footprint | Package | MPN | DNP | Mount_Type | Description | JLCPCB | JLCPCBURL | STANDARD | DigiKey | DigiKeyURL
C1 | 1 | 100nF | C_0603 |  |  |  | smt | Unpolarized capacitor | C1591 | https://jlcpcb.com/partdetail/1943-CL10B104KB8NNNC/C1591
J1 | 1 | SCL | PIN_HEADERS_1X01 |  |  |  | tht
J2 | 1 | SDA | PIN_HEADERS_1X01 |  |  |  | tht
J3 | 1 | +5V | PIN_HEADERS_1X01 |  |  |  | tht
J4 | 1 | GND | PIN_HEADERS_1X01 |  |  |  | tht
S1 | 1 | Temp sensor -55°C ~ 150°C | WSON-6_2x2mm_nopad |  | TMP117AIDRVR |  | smt | Temperature Sensor Digital, Local -55°C ~ 150°C 16 b 6-WSON (2x2) | C699536 | https://jlcpcb.com/partdetail/TexasInstruments-TMP117AIDRVR/C699536 | IPC 7351B | 296-51834-1-ND | https://www.digikey.com/en/products/detail/texas-instruments/TMP117AIDRVR/9685284

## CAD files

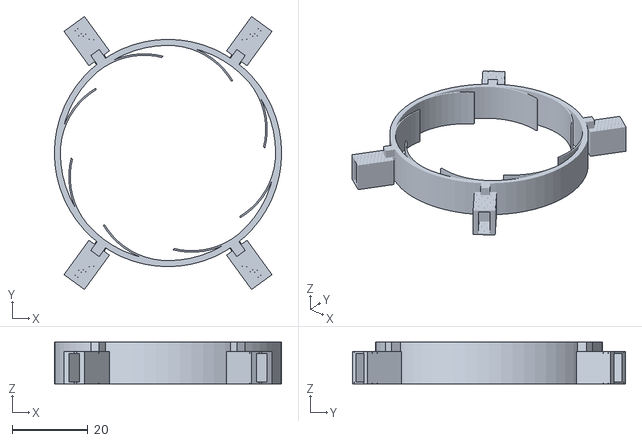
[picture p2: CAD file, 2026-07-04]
prints/stl/micrologger_adapter_serum160_tight_nozzle_0.4mm.stl
60.2 x 72.3 x 11.0

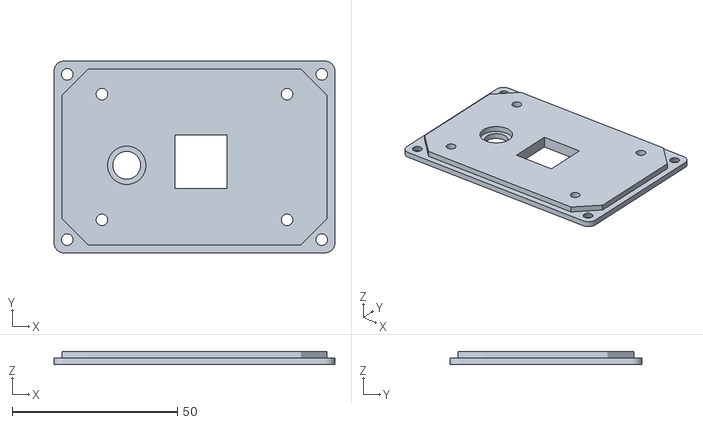
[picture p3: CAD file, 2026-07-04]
prints/stl/micrologger_controller_back_nozzle_0.5mm.stl
85.0 x 58.0 x 4.00

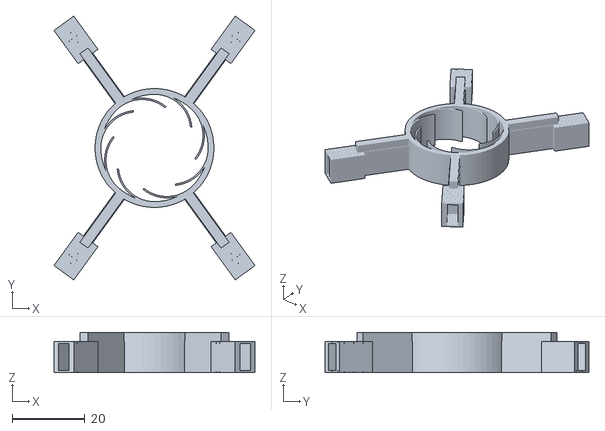
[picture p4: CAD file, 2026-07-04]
prints/stl/micrologger_adapter_culture60_tight_nozzle_0.4mm.stl
55.1 x 72.3 x 11.0

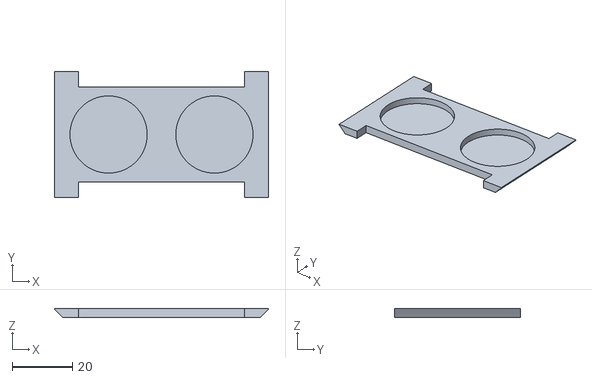
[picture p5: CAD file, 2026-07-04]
prints/stl/micrologger_controller_magnet_holder_nozzle_0.5mm.stl
70.8 x 41.6 x 2.84

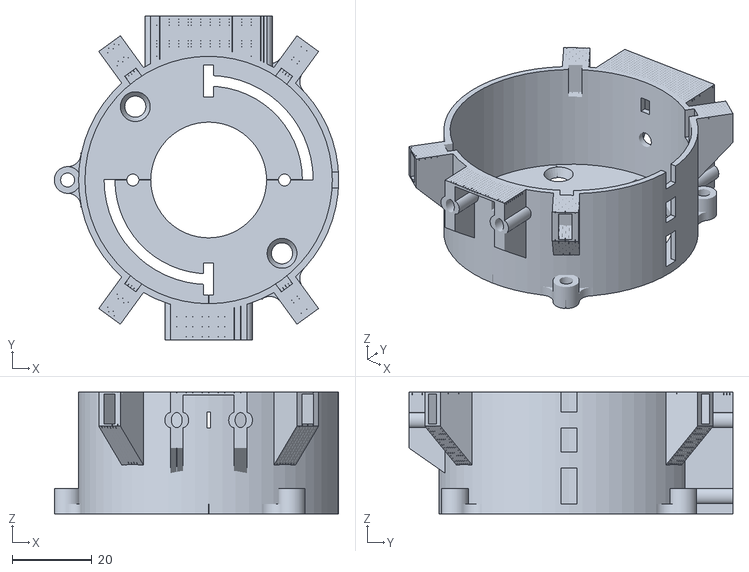
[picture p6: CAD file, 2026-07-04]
prints/stl/micrologger_device_nozzle_0.4mm.stl
71.3 x 81.2 x 30.5

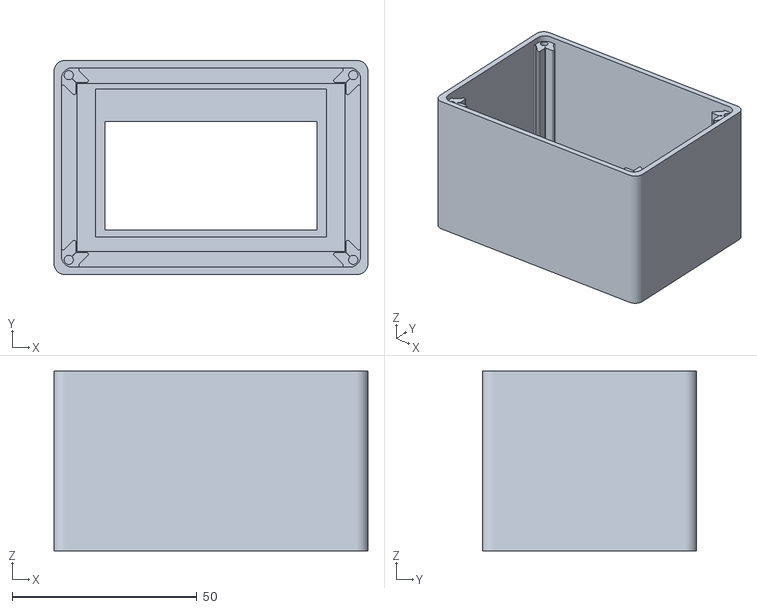
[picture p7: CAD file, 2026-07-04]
prints/stl/micrologger_controller_body_nozzle_0.5mm.stl
85.0 x 58.0 x 48.6

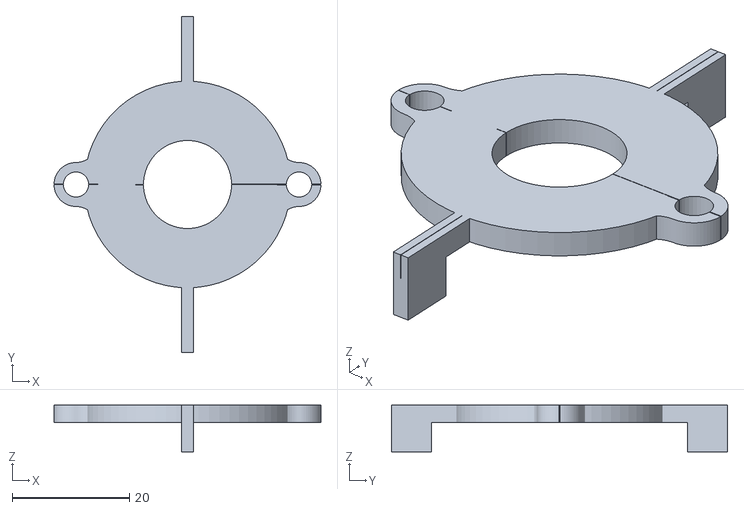
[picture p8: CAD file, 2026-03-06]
prints/stl/micrologger_base_bottle_adapter_nozzle_0.4mm.stl
45.5 x 57.3 x 8.00

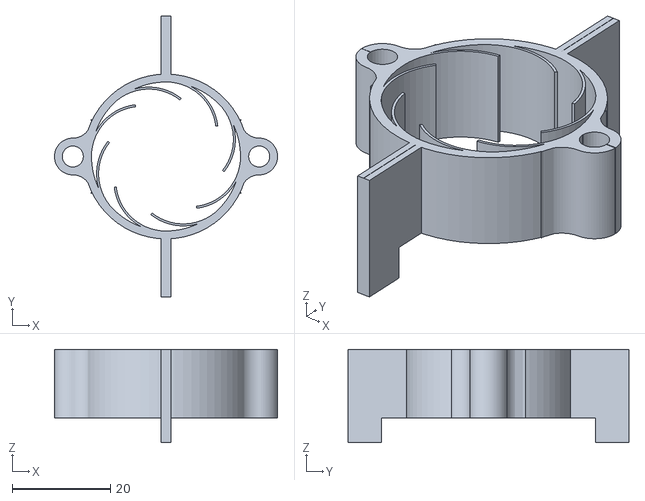
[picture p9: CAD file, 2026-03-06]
prints/stl/micrologger_base_adapter_culture60_nozzle_0.4mm.stl
45.5 x 57.3 x 19.0

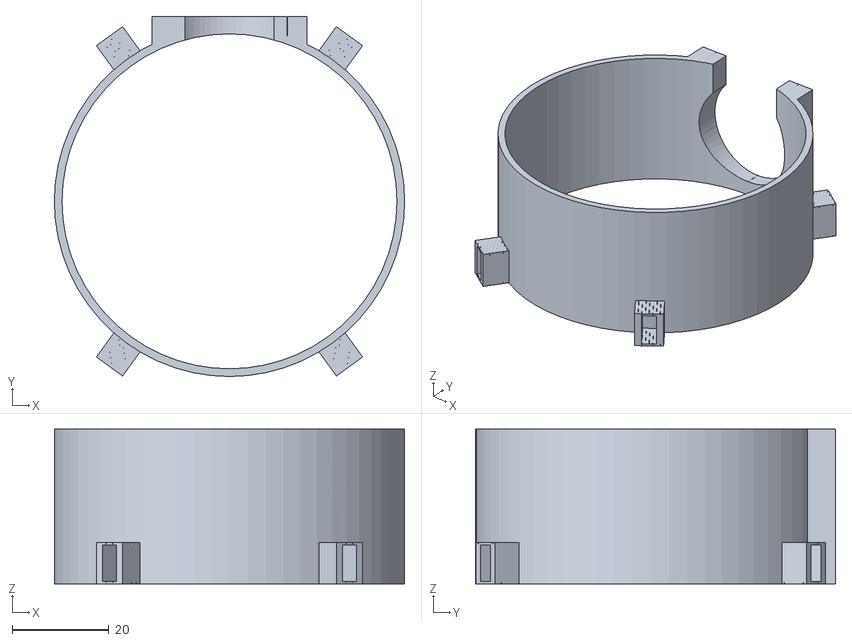
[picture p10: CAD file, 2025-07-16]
prints/stl/micrologger_light_adapter_up_nozzle_0.4mm.stl
72.5 x 74.5 x 32.0

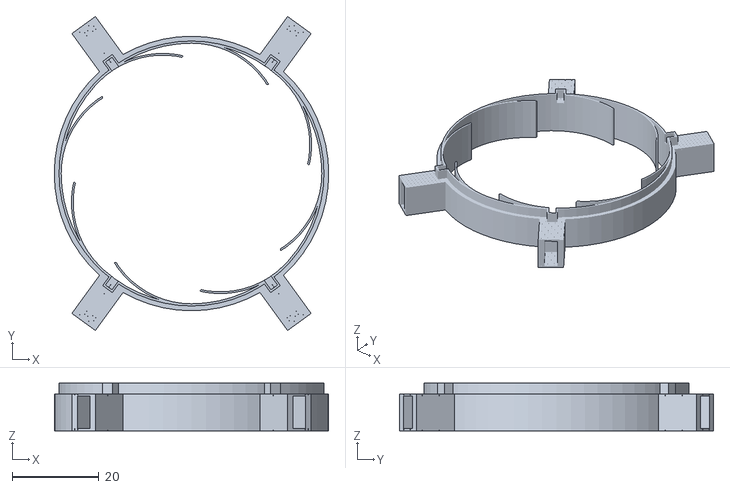
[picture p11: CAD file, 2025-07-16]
prints/stl/micrologger_adapter_gl45_nozzle_0.4mm.stl
63.2 x 72.3 x 11.0

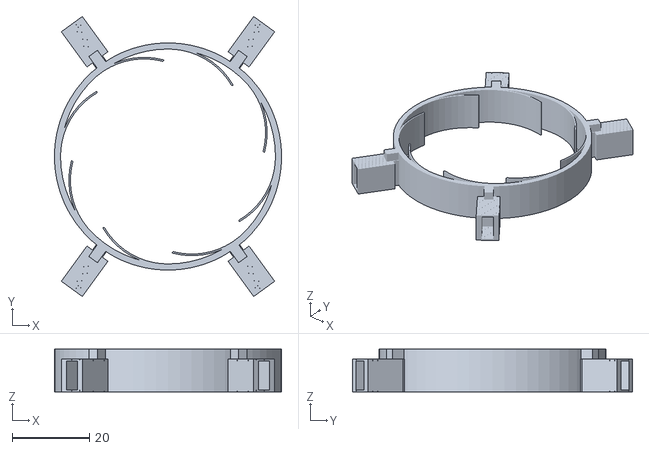
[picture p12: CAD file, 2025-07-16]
prints/stl/micrologger_adapter_serum120_nozzle_0.4mm.stl
58.7 x 72.3 x 11.0

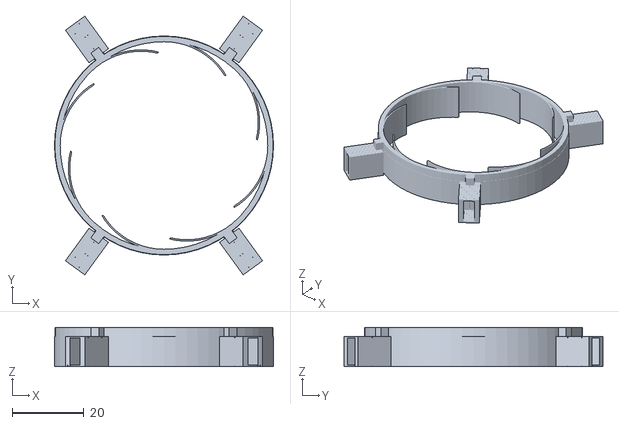
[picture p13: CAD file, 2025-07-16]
prints/stl/micrologger_adapter_serum160_nozzle_0.4mm.stl
61.2 x 72.3 x 11.0

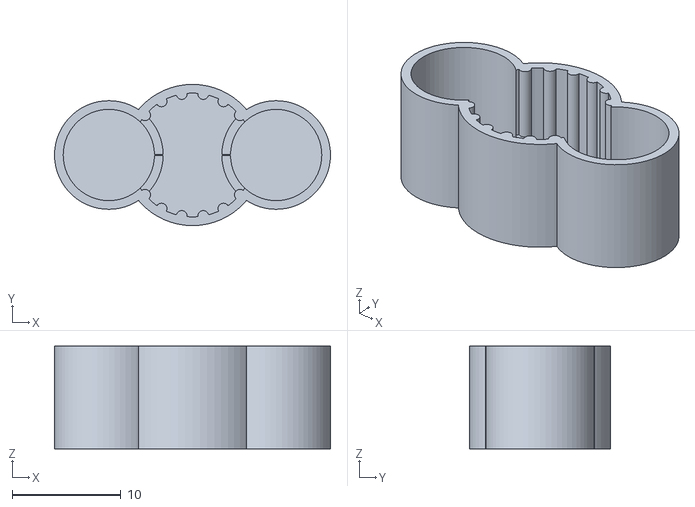
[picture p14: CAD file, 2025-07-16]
prints/stl/micrologger_stirrer_nozzle_0.4mm.stl
25.4 x 13.0 x 9.45

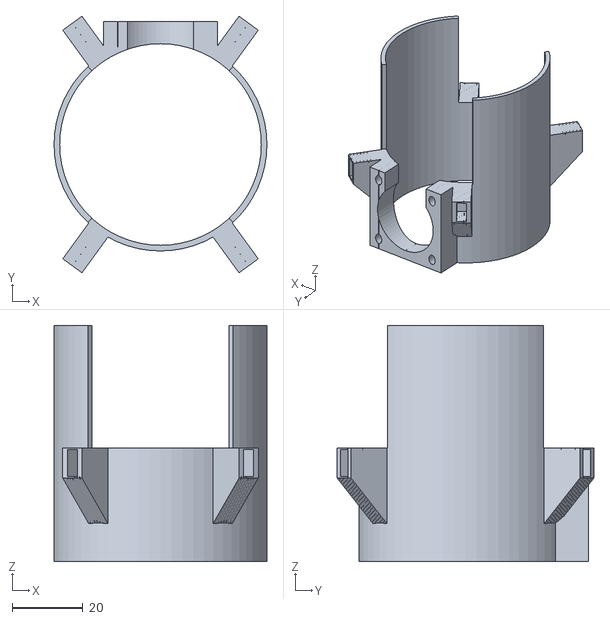
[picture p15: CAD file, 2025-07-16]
prints/stl/micrologger_light_adapter_down_nozzle_0.4mm.stl
60.0 x 72.3 x 66.5

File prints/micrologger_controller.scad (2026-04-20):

use <utils.scad>;
use <screws.scad>;

// constants
$e = 0.01; // small extra for removing artifacts during differencing
$2e = 2 * $e; // twice epsilon for extra length when translating by -e
$fn = $preview ? 10 : 60; // number of default vertices when rendering cylinders
nylon_tol = 0.1; // extra tolerance for carbon fibre nylon parts shrinkage
tglase_tol = 0.025; // extra tolerance for tglase parts

// sizes
//$extra_tolerance = 2 * nylon_tol; // for cutouts, screws, etc.
$extra_tolerance = 2 * tglase_tol; // for cutouts, screws, etc.
$extra_tolerance_2D = [$extra_tolerance, $extra_tolerance]; // tolerance in 2 d
$screw_hole_tolerance = 0.45 + $extra_tolerance; // tolerance for screw holes
$screw_threadable_tolerance = 0; // tolerance for screw holes that can be threaded into

// controller box (designed for print with a 0.5 mm nozzle)
// depth:
//  - display recess: 1.0 mm
//  - display + board height: 4.0mm
//  - standoff: 28.0 mm
//  - pcb: 1.6mm
//  - standoffs: 12mm (has to be M3, M2.5 doesn't have this length)
//  - back wall: 4.0 mm
//  total: 50.6
//  - barrel jack: 12.4mm from board to wall
// --> indent the plug by 0.4 mm
//  - RJ45: 16.2mm from board to plug --> should work well with 12mm standoff

$box_size = [85, 58, 50.6]; //$box_size = [85, 58, 50];
$box_wall_thickness = 2; // thickness of the box walls
$box_front_thickness = 4; // front thickness
$box_corner_radius = 3; // radius of the corners
$box_back_thickness = $box_front_thickness; // thickness of the back wall
$box_back_wall_gap = 0.3 + $extra_tolerance; // gap between the back insent and the walls
$box_back_attachment_screws_indent = 4; // indentation from the edge
$box_back_attachment_screws_gap = 0.1; // gap in the screw sockets

// oled
$oled_screen = [57.3, 29.3] + 2 * $extra_tolerance_2D;
$oled_screen_offset = [0, -2.2]; // offset from center of board
$oled_display = [62.5, 40.0] + 2 * $extra_tolerance_2D;
$oled_display_recessed = 1.0; // recess from screen
$oled_display_offset = [0, 1.2]; // offset from center of board
$oled_board = [72.5, 45.5]; // oled board size (plus space for screws)
$oled_board_recessed = 0.5; // recess from display

// magnet adapters
$magnet_adapter_width = 4; // adapter width
$magnet_adapter_depth = 4;
$magnet_adapter_corner_radius = 0.5;
$magnet_adapter_tolerance = 0.2; // tolerance between adapter and insert
$magnet_adapter_height_gap = 1.0; // how much space to leave in the adapter height
$magnet_diameter = 25.4 + 3 * $extra_tolerance; // this is the 1" diameter
$magnet_thickness_0_1 = 2.54; // this is the 1/10" thick
$magnet_thickness_0_125 = 3.18; // this is the 1/8" thick
$magnet_wall_thickness = 3; // how thick are the walls around the magnets
$magnet_base_thickness = 0.5; // how thick is the base of the magnet holder
$magnet_distance = 35; // distance between magnets

// pcb, power, ethernet, antenna
$pcb_screws_position = [28, 19]; // x/y coordinates relative to center
$pcb_screws_offset = 0.75; // offset from the back wall
$power_jack_position = [-20.5, -2.5]; // x/y coordinates relative to center
$power_jack_thread_diameter = 8.1 + 0.2 + 2 * $extra_tolerance;
$power_jack_support_diameter = 11.3 + 0.2 + 2 * $extra_tolerance;
$power_jack_support_offset = $box_back_thickness - 2.0; // offset from back wall
$ethernet_position = [2, -1.47]; // x/y coordinates relative to center
$ethernet_cutout = [15.5, 15.9] + [0.2, 0.2] + 2 * $extra_tolerance_2D;

// antenna best placed inside housing (on back wall) and design of P2 antenna not conducive to going through a cutout
//$antenna_position = [$box_size[0]/2 - 1.5 - $box_back_wall_gap/2 - $box_wall_thickness, 12];
//$antenna_cutout = [3, 9];

// controller back
module module_controller_back() {
  difference() {
    union() {
      // back wall
      linear_extrude(height = $box_wall_thickness)
        offset(r = $box_corner_radius)
          offset(delta = -$box_corner_radius)
            square([$box_size[0], $box_size[1]], center = true);
      // elevated back center
      x = $box_size[0] - 2 * $box_wall_thickness - 2 * $box_back_wall_gap;
      y = $box_size[1] - 2 * $box_wall_thickness - 2 * $box_back_wall_gap;
      edge = 2 * $box_back_attachment_screws_indent;
      linear_extrude(height = $box_back_thickness)
        polygon([
            [x/2 - edge, y/2], [x/2, y/2 - edge],
            [x/2, -y/2 + edge], [x/2 - edge, -y/2],
            [-x/2 + edge, -y/2], [-x/2, -y/2 + edge],
            [-x/2, y/2 - edge], [-x/2 + edge, y/2]
          ]);

    }

    // back wall attachments screws
    for (x = [-1, 1]) {
      for (y = [-1, 1]) {
        translate([-x * ($box_size[0]/2 - $box_back_attachment_screws_indent), y * ($box_size[1]/2 - $box_back_attachment_screws_indent), -$e])
          machine_screw(name = "M2.5", length = $box_back_thickness + $2e, tolerance = $screw_hole_tolerance);
      }
    }

    // power jack cutout
    translate([$power_jack_position[0], $power_jack_position[1], -$e])
      cylinder(d = $power_jack_thread_diameter, h = $box_back_thickness + $2e);
    translate([$power_jack_position[0], $power_jack_position[1], $power_jack_support_offset])
      cylinder(d = $power_jack_support_diameter, h = $box_back_thickness);

    // ethernet cutout
    translate([$ethernet_position[0], $ethernet_position[1], -$e])
      xy_center_cube([$ethernet_cutout[0], $ethernet_cutout[1], $box_back_thickness + $2e]);

    // antenna cutout
    /*
    translate([$antenna_position[0], $antenna_position[1], -$e])
      xy_center_cube([$antenna_cutout[0], $antenna_cutout[1], $box_back_thickness + $2e]);
    */

    // pcb support screws
    for (x = [-1, 1]) {
      for (y = [-1, 1]) {
        translate([x * $pcb_screws_position[0], y * $pcb_screws_position[1], -$e])
          machine_screw(name = "M2.5", length = $box_back_thickness + $2e, tolerance = $screw_hole_tolerance);
      }
    }

  }
}

// controller front
module module_controller_front() {
  // construct the front
  difference() {
    union() {
      // box walls
      difference() {
        // box with rounded edges
        linear_extrude(height = $box_size[2] - $box_wall_thickness)
          offset(r = $box_corner_radius)
            offset(delta = -$box_corner_radius)
              square([$box_size[0], $box_size[1]], center = true);
        // inside cutout
        translate([0, 0, $box_front_thickness])
          linear_extrude(height = $box_size[2])
            offset(r = $box_corner_radius)
              offset(delta = -$box_corner_radius)
                square([$box_size[0] - 2 * $box_wall_thickness, $box_size[1] - 2 * $box_wall_thickness], center = true);
      }

      // magnet attachments long edge
      for (x = [-1, 1])
        translate([0, x * ($box_size[1]/2 - $magnet_adapter_depth/2 - $box_wall_thickness), $box_front_thickness])
        mirror([0, if (x == -1) 1 else 0, 0])
        module_controller_magnet_adapters(
          width = $box_size[0] - 2 * $box_wall_thickness - 2 * $magnet_adapter_depth,
          height = $box_size[2] - $box_front_thickness - $box_back_thickness - $extra_tolerance
        );

      // magnet attachments short edge
      for (y = [-1, 1])
        translate([y * ($box_size[0]/2 - $magnet_adapter_depth/2 - $box_wall_thickness), 0, $box_front_thickness])
        mirror([if (y == 1) 1 else 0, 0, 0])
        rotate([0, 0, 90])
        module_controller_magnet_adapters(
          width = $box_size[1] - 2 * $box_wall_thickness - 2 * $magnet_adapter_depth,
          height = $box_size[2] - $box_front_thickness - $box_back_thickness - $extra_tolerance
        );

      // corner pillars
      for (y = [-1, 1]) for (x = [-1, 1])
        translate([y * ($box_size[0]/2 - $magnet_adapter_depth/2 - $box_wall_thickness), x * ($box_size[1]/2 - $magnet_adapter_depth/2 - $box_wall_thickness), $box_front_thickness])
          xy_center_cube([$magnet_adapter_depth + $2e, $magnet_adapter_depth + $2e, $box_size[2] - $box_front_thickness - $box_back_thickness - $extra_tolerance]);
    }

    // back wall attachments screws
    for (x = [-1, 1]) {
      for (y = [-1, 1]) {
        translate([x * ($box_size[0]/2 - $box_back_attachment_screws_indent), y * ($box_size[1]/2 - $box_back_attachment_screws_indent), $box_front_thickness])
          machine_screw(name = "M2.5", length = $box_size[2] - $box_front_thickness - $box_back_thickness + $e, countersink = false, tolerance = $screw_threadable_tolerance);
      }
    }
    // attachment screw gaps (for better print paths)
    for (y = [-1, 1]) for (x = [-1, 1])
      translate([y * ($box_size[0]/2 - $magnet_adapter_depth - $box_wall_thickness), x * ($box_size[1]/2 - $magnet_adapter_depth - $box_wall_thickness), $box_front_thickness])
        rotate([0, 0, -y * x * 45])
          xy_center_cube([$box_back_attachment_screws_gap, $magnet_adapter_depth, $box_size[2] - $box_front_thickness - $box_back_thickness + $e]);
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

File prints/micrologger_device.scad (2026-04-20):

use <utils.scad>;
use <screws.scad>;

// constants
$e = 0.01; // small extra for removing artifacts during differencing
$2e = 2 * $e; // twice epsilon for extra length when translating by -e
$fn = $preview ? 10 : 60; // number of default vertices when rendering cylinders
nylon_tol = 0.1; // extra tolerance for carbon fibre nylon parts shrinkage
tglase_tol = 0.025; // extra tolerance for tglase parts

/** device general settings **/

$extra_tolerance = 2 * nylon_tol; // for cutouts, screws, etc.
//$extra_tolerance = 2 * tglase_tol; // for cutouts, screws, etc.
$extra_tolerance_2D = [$extra_tolerance, $extra_tolerance]; // tolerance in 2 d
$screw_hole_tolerance = 0.45 + $extra_tolerance; // tolerance for screw holes
$screw_threadable_tolerance = 0; // tolerance for screw holes that can be threaded into
$screw_vertical_stretch = 0.5; // vertical stretch
$layer_height = 0.25;
$spokes = 0.05; // width of print enhancement spokes
$nozzle = 0.4; // nozzle width for spacing decisions
$n_walls = 8; // number of walls printed

// holder overall sizes
$holder_inner_diameter = 62; // fix inner diameter for adapter compability
$holder_inner_radius = $holder_inner_diameter/2;
$wall = 4 * $nozzle; // thickness of all walls
$holder_bottom_thickness = 2.5; // thickness of base
$holder_base_height = 14;
$holder_sensors_height = 14;
$holder_total_height = $holder_bottom_thickness + $holder_base_height + $holder_sensors_height;
$holder_feet_screw_type = "6-32"; // what screw type for the feet
$holder_feet_screw_thread_height = 6.35; // 1/4" length
$holder_feet_screw_wall = $wall; // thickness of the wall around the feet threads
$holder_feet_location = [54, 180, 306]; // angle locations
$holder_gap_width = 4; // gap for bottle view
$holder_feet_diameter = get_screw($holder_feet_screw_type)[1] + 2 * $holder_feet_screw_wall;
$holder_vent_diameter = $holder_inner_diameter - 15;
$holder_vent_width = 2.7;
$holder_notch_width = 2.5;
$holder_notch_length = 8;
$holder_notch_position = $holder_vent_diameter/2 + $holder_vent_width/2;
$holder_base_adapter_screws_distance = 38; // distance between the screws
$holder_base_adapter_screws_type = "M3"; // screw type

// stirrer
$stirrer_hole_diameter = 29; // diameter of the center hole for the magnetic stirrer (fits the largest stirrer at ~27mm)
$stirrer_screw_type = "M4"; // what type of screw type for stirrer attachment
$stirrer_screw_distance = 52; // distance between the screws
$stirrer_screw_rotation = 135; // how much to rotate (counter clockwise)

// sensor and beam
$block_attachment_screws_diameter = get_screw("M3")[1] - 0.25; // screws diameter
$beam_position_z = 7; // from top
$light_tunnel_height = 4.0; // height of the light tunnel (photodiode area cross section ~ 3.35mm)
$sensor_light_tunnel_width = 2.75; // width of the sensor light tunnel (photodiode area cross section ~ 3.35mm)
$sensor_block_roof = 3 * $layer_height;
$sensor_block_floor = 2 * $layer_height; // 1 layer at the bottom
$sensor_block_roof_min = 1 * $layer_height; // min height of the sloping roof (at outer edge)
$sensor_block_roof_angle = 25; // angle of roof [in degrees]
$sensor_block_screws_x = 13; // +/- from center
$sensor_block_screws_z = [$beam_position_z, 26]; // from top
$sensor_block_depth = 8.5;
$sensor_block_total_depth = $holder_inner_radius + $wall + $sensor_block_depth;
$sensor_block_outer_width = 2 * $sensor_block_screws_x + $spokes + 2 * $wall;
$sensor_block_inner_width = 2 * $sensor_block_screws_x - $spokes - 2 * $wall;
$sensor_columns_width = 11.0; // columns left/right of sensors
$sensor_columns_start = 15.0; // where the columns start
$beam_light_tunnel_width = 0.8; // width of light tunnel (same hight as sensor block)
$beam_block_roof = 3 * $layer_height; // $sensor_block_floor;
$beam_block_roof_min = $sensor_block_roof_min;
$beam_block_roof_angle = $sensor_block_roof_angle;
$beam_block_screws_x = 8; // +/- from center
$beam_block_screws_z = $beam_position_z; // from top
$beam_block_height = 14; // from top
$beam_block_depth = 7.5;
$beam_block_total_depth = $holder_inner_radius + $wall + $beam_block_depth;
$beam_block_outer_width = 2 * $beam_block_screws_x + $spokes + 2 * $wall;
$beam_block_inner_width = 2 * $beam_block_screws_x - $spokes - 2 * $wall;

// ir temp sensor
$temp_position_z = 17; // from top
$temp_tunnel_diameter = 4.0; // diameter of sensor entrance

/** micrologger device **/

// FIXME: use the spokes distribution functions used in the base adapters
module device(spokes = true) {

  difference() {

    union() {
      // ring
      with_base_magnets(top = $holder_total_height, spokes = spokes, ridges = true, last_layer = true)
        cylinder(d = $holder_inner_diameter + 2 * $wall, h = $holder_total_height);

      // feet threads
      for (angle = $holder_feet_location) {
        translate([$holder_inner_radius * cos(angle), $holder_inner_radius * sin(angle), 0])
        rotate([0, 0, 90 + angle])
        translate([0, -$holder_feet_diameter/2 - 1, 0])
        difference() {
          // foot
          union() {
            // thread core
            linear_extrude($holder_bottom_thickness)
              translate([-$holder_feet_diameter/2, 0, 0])
                square([$holder_feet_diameter, $holder_feet_diameter/2]);
            linear_extrude($holder_feet_screw_thread_height)
              circle(d = $holder_feet_diameter);
            // smooth edges to ring for bottom
            linear_extrude($holder_bottom_thickness)
            for (x = [0, 1]) {
              mirror([x, 0, 0])
                translate([$holder_feet_diameter/2, 0, 0])
                  difference() {
                    square($holder_feet_diameter/2);
                    translate([$holder_feet_diameter/2, 0, 0]) circle(d = $holder_feet_diameter);
                  }
            }
          }

          // foot thread hole
          translate([0, 0, -$e])
            cylinder(d = get_screw($holder_feet_screw_type)[1] + $screw_threadable_tolerance, h = $holder_feet_screw_thread_height + $2e);

          // foot base spokes
          if (spokes) {
            translate([-$spokes/2, -($holder_feet_diameter + $e)/2, -$e])
              cube([$spokes, $holder_feet_diameter + $2e, $holder_bottom_thickness + $e], center = false);
          }
        }
      }
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

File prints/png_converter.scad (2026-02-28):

// import the passed in stl file path
import(stl);

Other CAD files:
prints/stl/micrologger_adapter_hungate_nozzle_0.4mm.stl
prints/stl/micrologger_adapter_balch_nozzle_0.4mm.stl
prints/stl/micrologger_adapter_culture60_nozzle_0.4mm.stl
prints/stl/micrologger_adapter_serum60_nozzle_0.4mm.stl
prints/screws.scad
pcbs/sensor_board_pcb_v77_schematic_v52.f3d
prints/utils.scad

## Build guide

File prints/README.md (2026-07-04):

<!-- README.md is generated from README.Rmd. Please edit that file -->

# 3D printed µLogger parts

## Device



## Adapter Balch

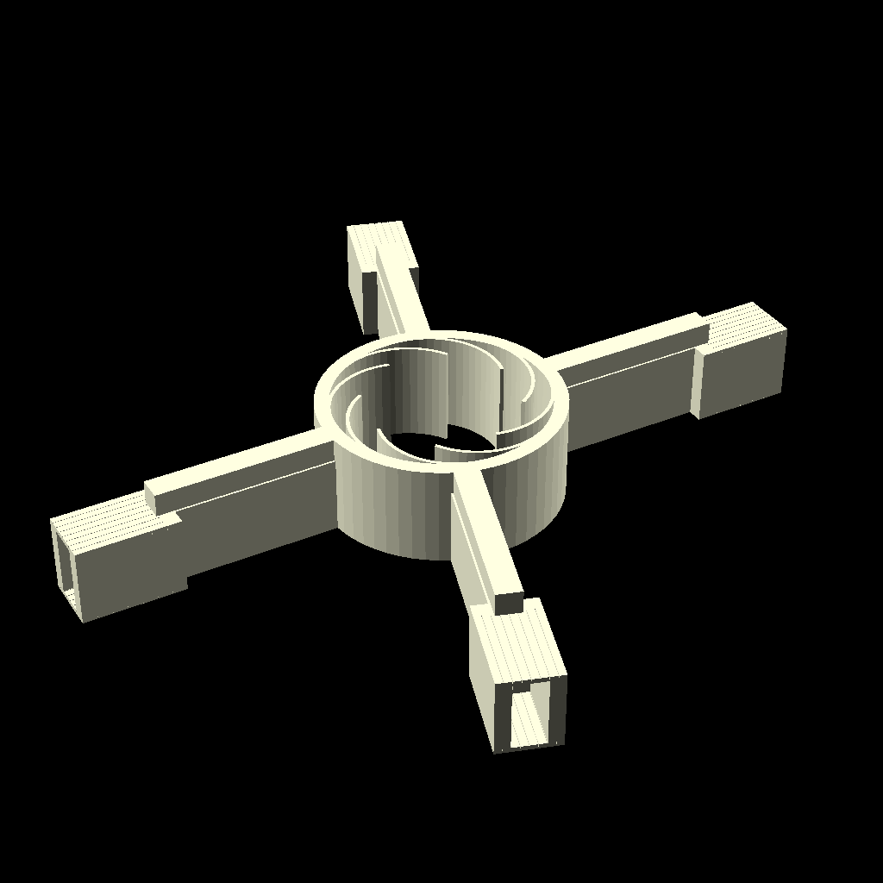
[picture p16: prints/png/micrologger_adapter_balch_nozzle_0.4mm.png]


## Adapter Culture60

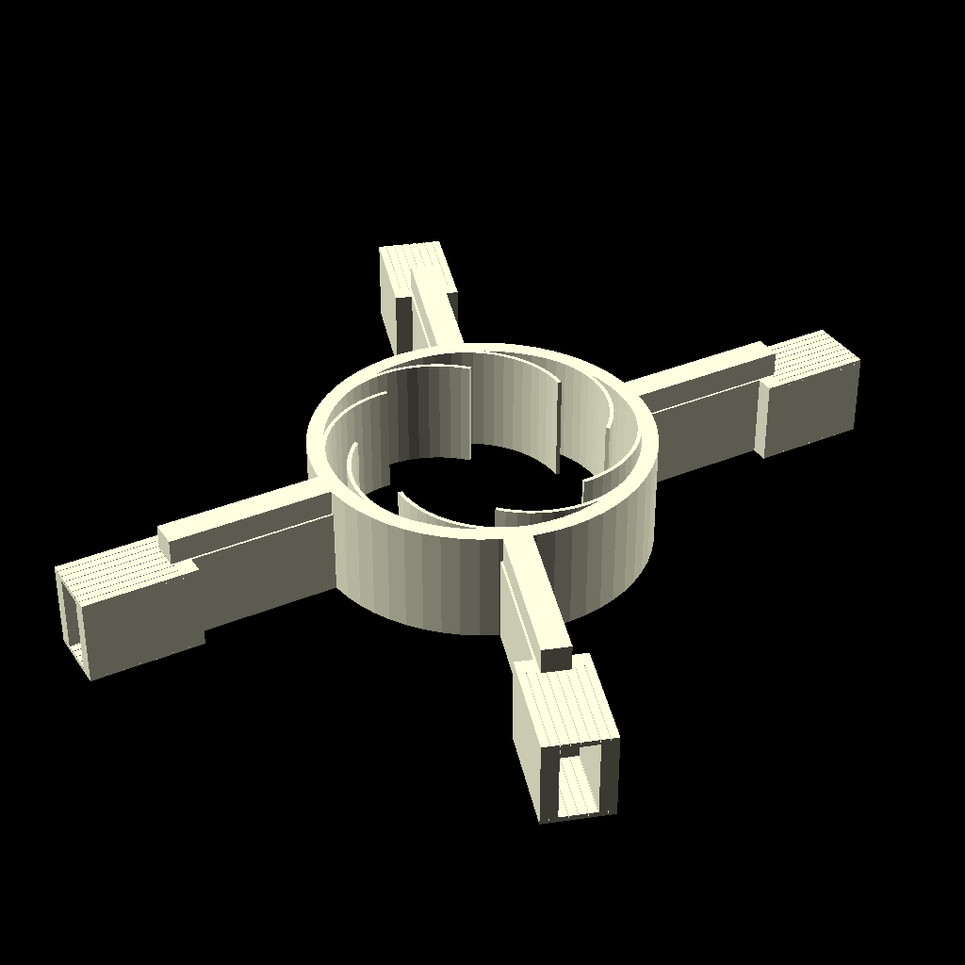
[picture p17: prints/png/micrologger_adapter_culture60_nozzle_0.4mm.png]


## Adapter Culture60 Tight

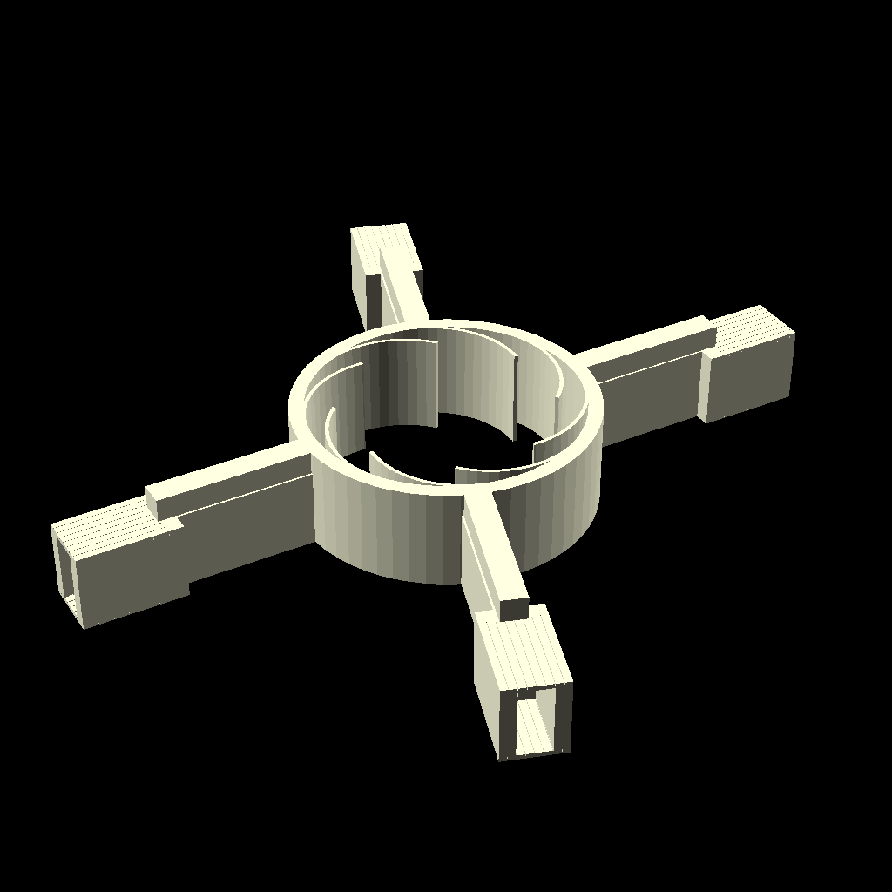
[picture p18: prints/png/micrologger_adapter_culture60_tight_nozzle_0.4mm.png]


## Adapter Gl45

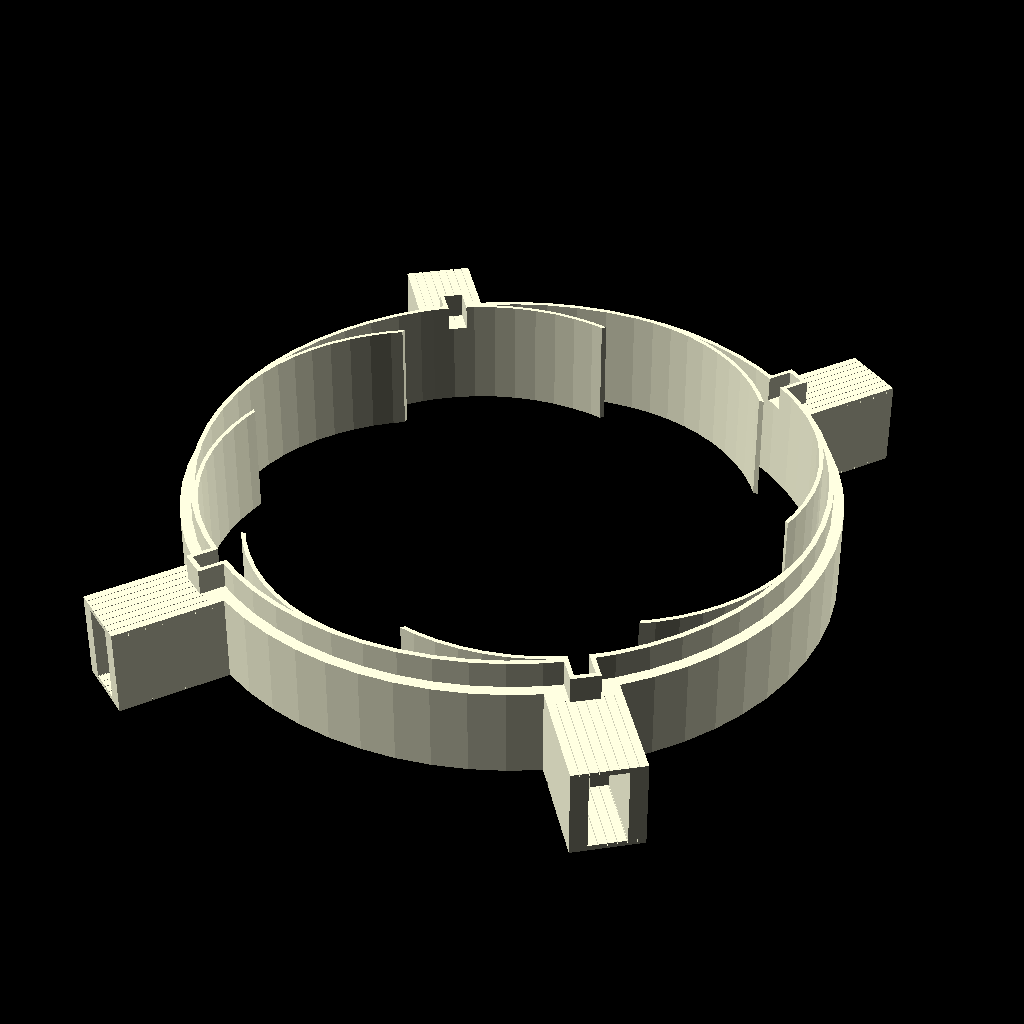
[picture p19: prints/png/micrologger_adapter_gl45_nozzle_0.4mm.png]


## Adapter Hungate

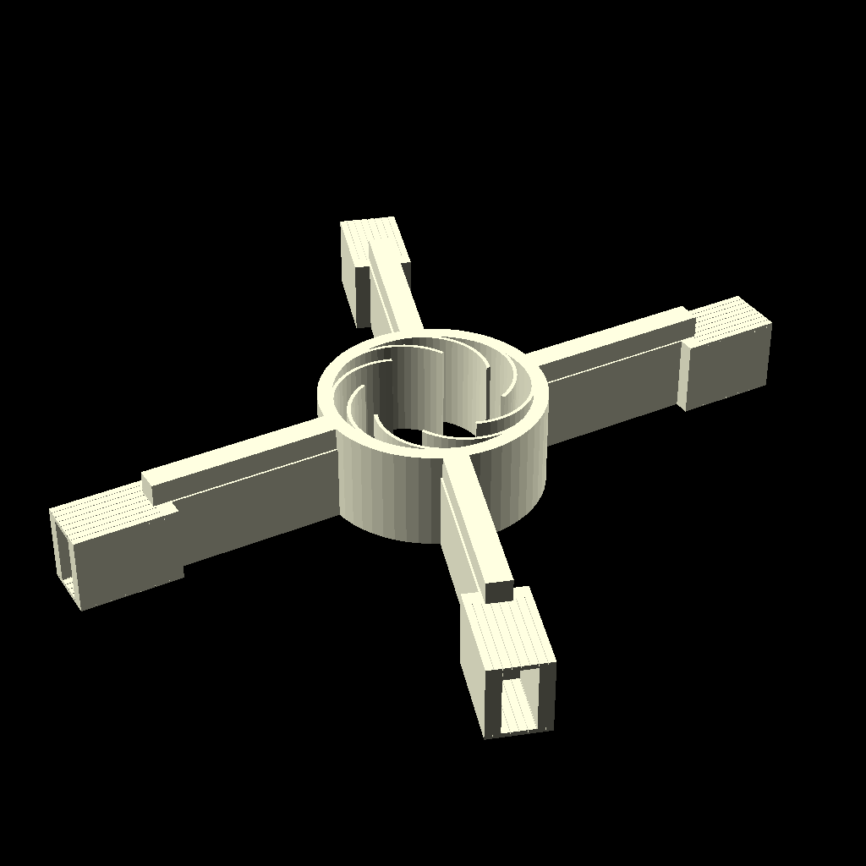
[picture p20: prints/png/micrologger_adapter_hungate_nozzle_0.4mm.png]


## Adapter Serum120

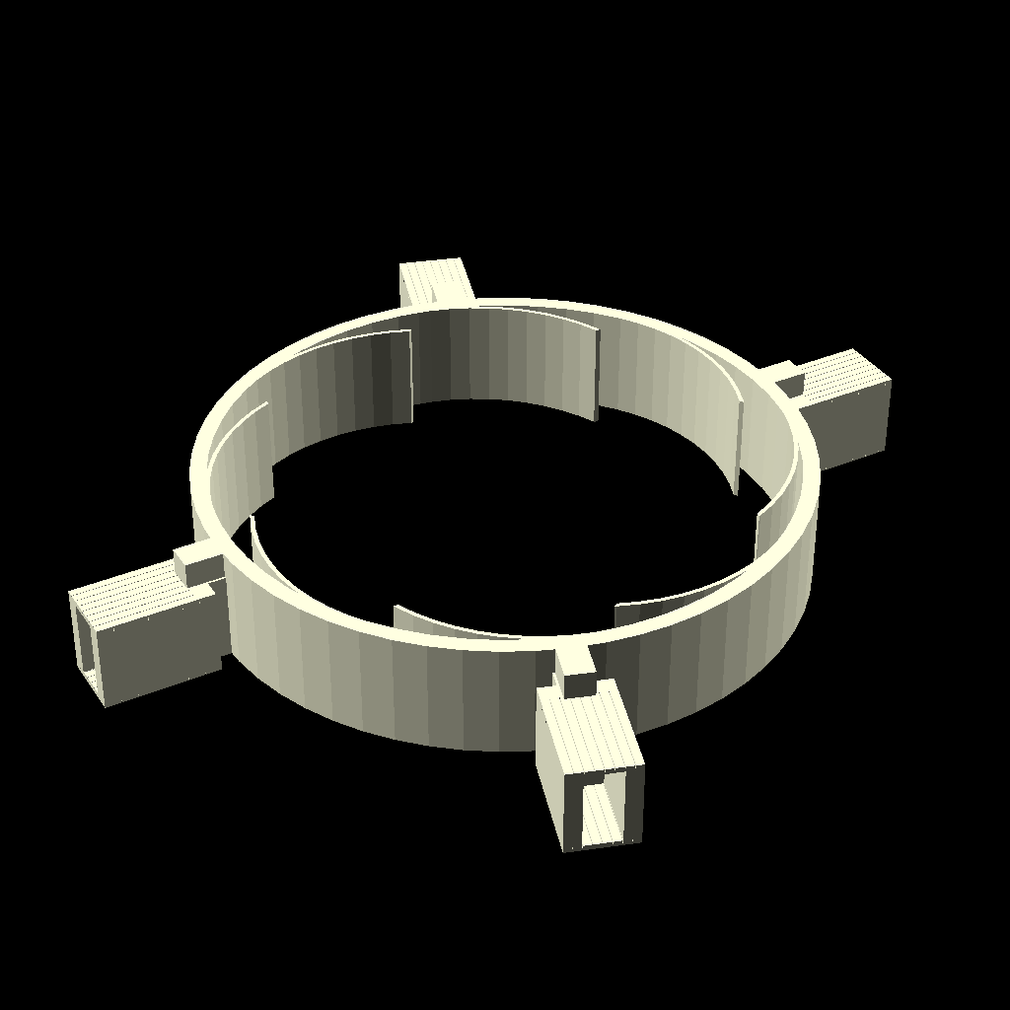
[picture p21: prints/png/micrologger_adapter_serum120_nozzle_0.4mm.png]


## Adapter Serum160

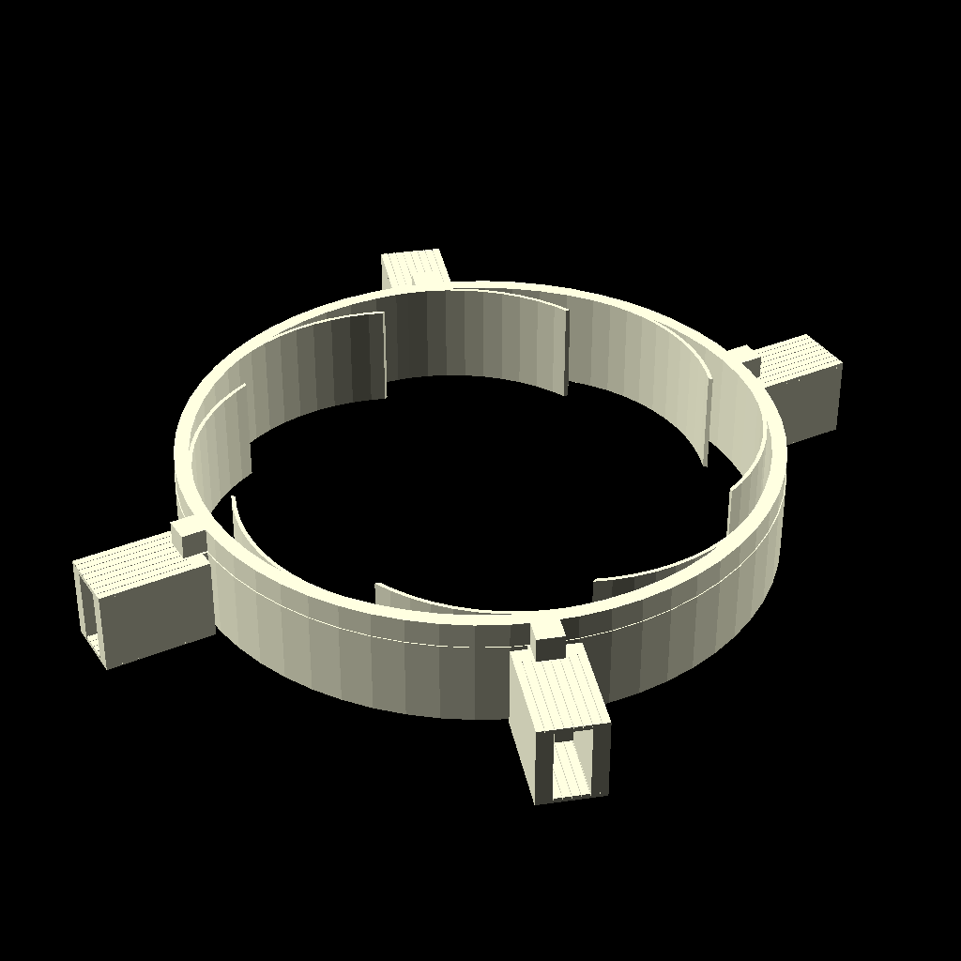
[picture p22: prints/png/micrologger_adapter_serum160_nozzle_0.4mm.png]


## Adapter Serum160 Tight

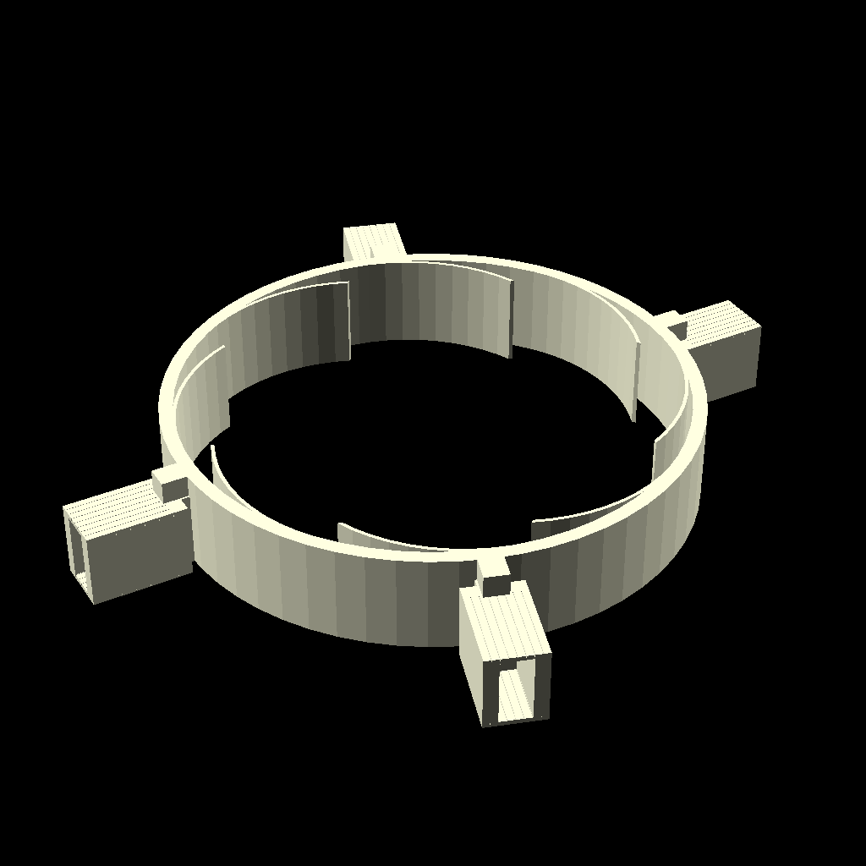
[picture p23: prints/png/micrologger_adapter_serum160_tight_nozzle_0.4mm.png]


## Adapter Serum60

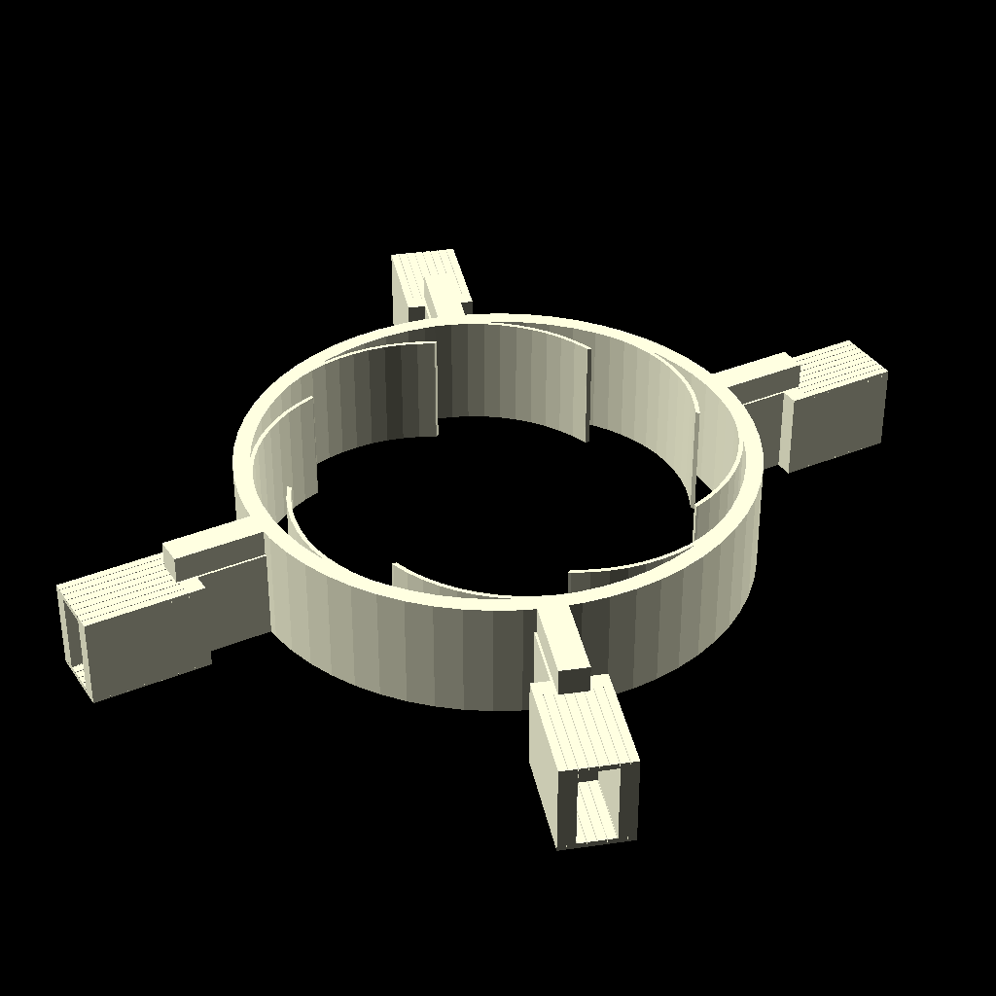
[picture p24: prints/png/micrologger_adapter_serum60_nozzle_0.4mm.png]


## Base Adapter Culture60

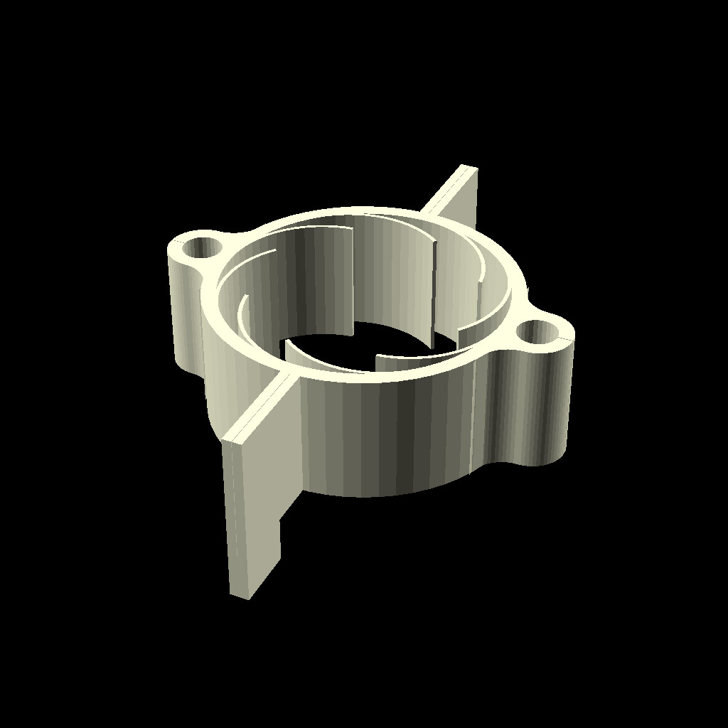
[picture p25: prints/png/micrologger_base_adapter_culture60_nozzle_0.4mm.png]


## Base Bottle Adapter

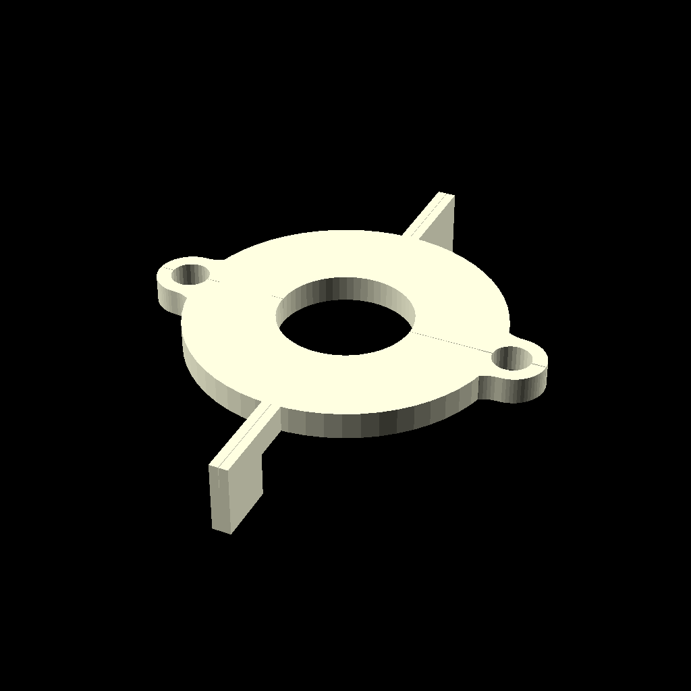
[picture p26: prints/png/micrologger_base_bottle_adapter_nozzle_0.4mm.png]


## Controller Back

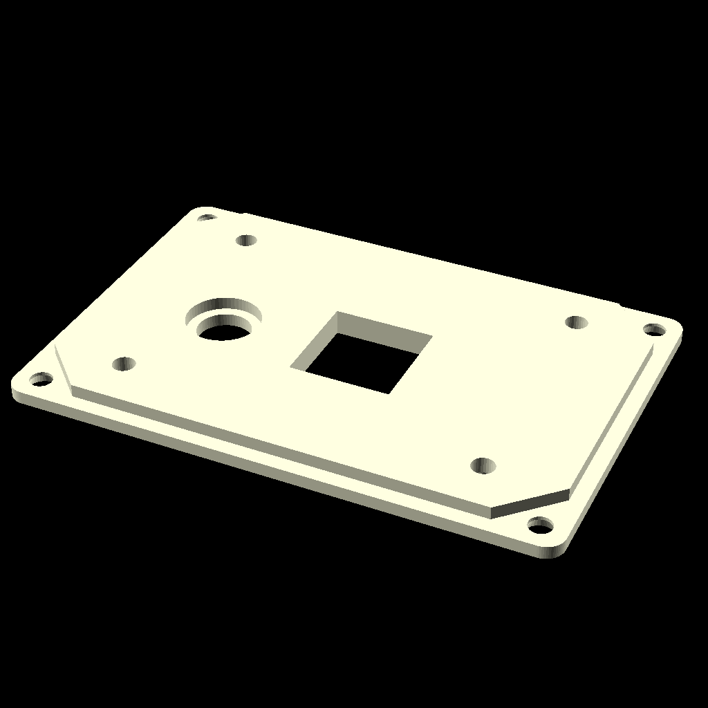
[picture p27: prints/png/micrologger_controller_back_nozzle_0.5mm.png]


## Controller Body

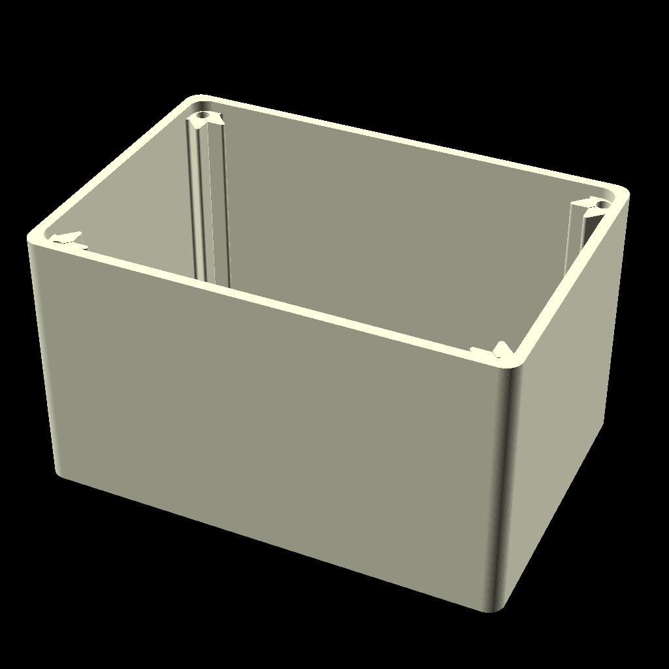
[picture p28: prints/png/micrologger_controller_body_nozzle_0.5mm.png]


## Controller Magnet Holder

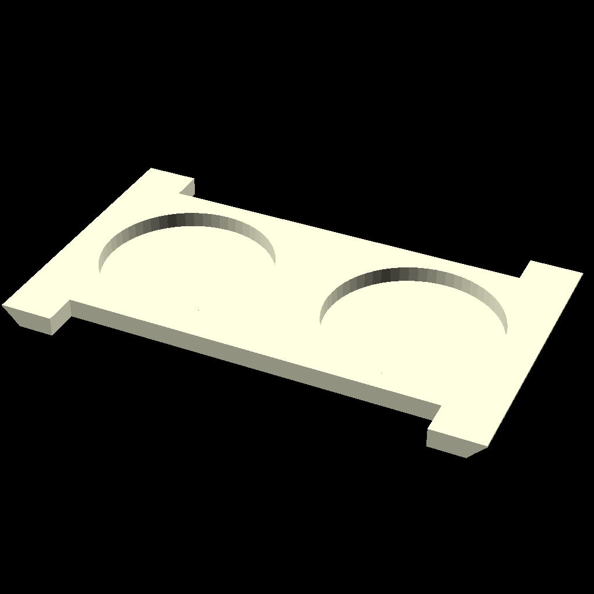
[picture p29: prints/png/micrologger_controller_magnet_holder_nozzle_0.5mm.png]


## Light Adapter Down

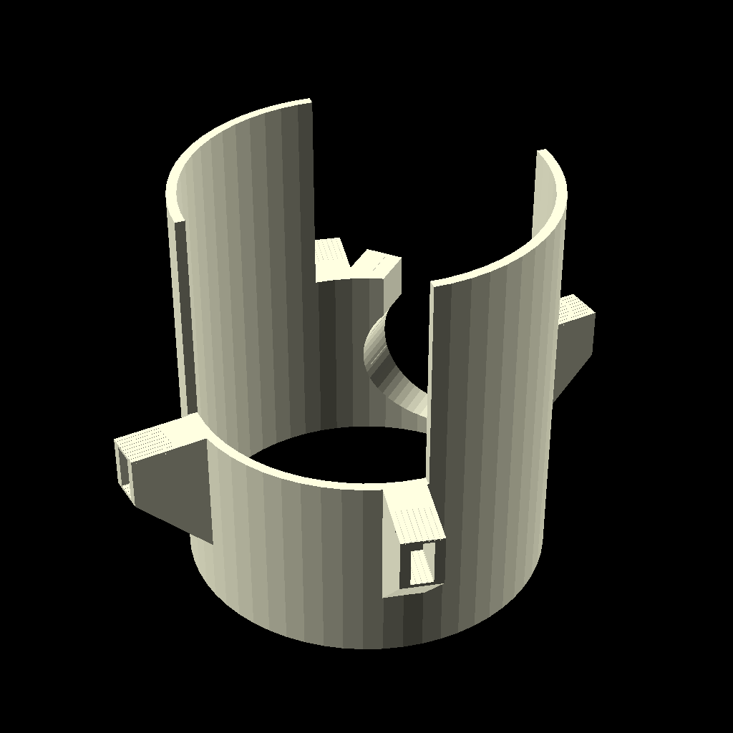
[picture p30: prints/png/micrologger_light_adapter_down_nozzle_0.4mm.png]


## Light Adapter Up

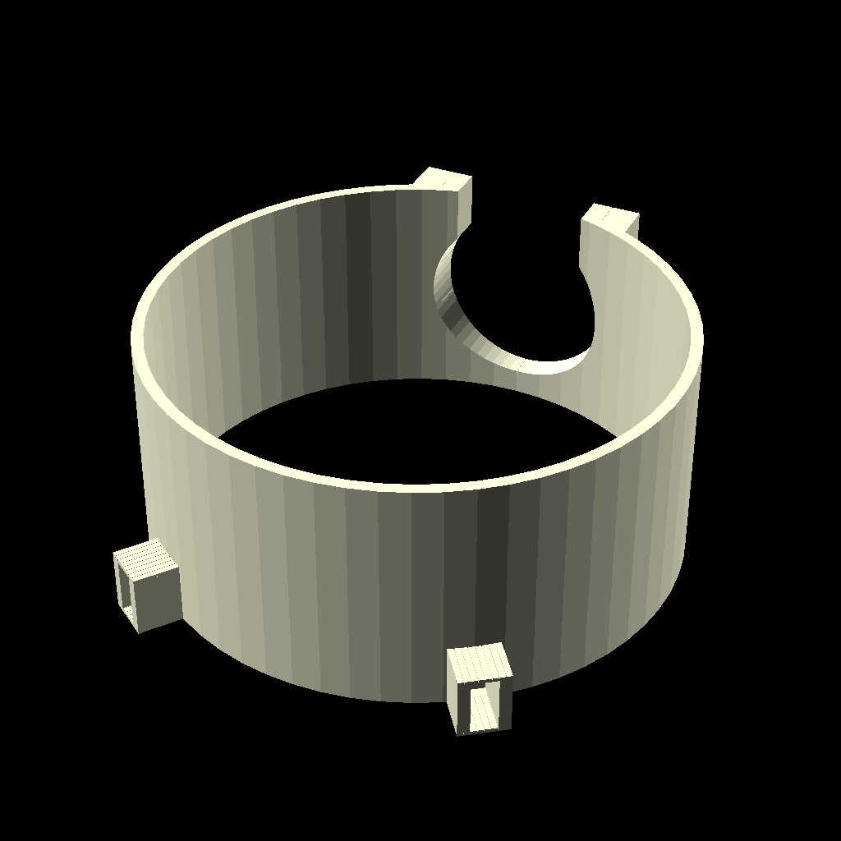
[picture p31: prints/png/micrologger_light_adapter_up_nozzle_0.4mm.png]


## Stirrer

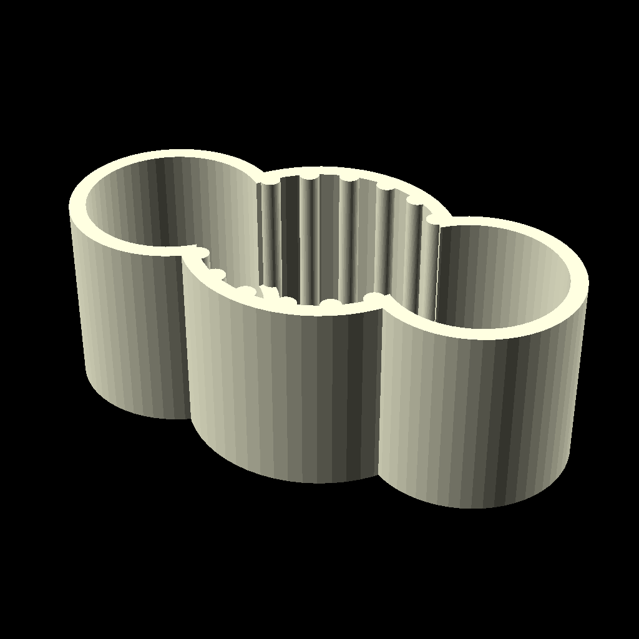
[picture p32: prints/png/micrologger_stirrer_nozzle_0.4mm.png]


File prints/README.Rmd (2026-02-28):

---
output: github_document
---

<!-- README.md is generated from README.Rmd. Please edit that file -->

```{r}
#| include: false
knitr::opts_chunk$set(
  collapse = TRUE,
  comment = "#>",
  fig.path = "man/figures/README-",
  out.width = "100%"
)
```

# 3D printed µLogger parts

```{r}
#| echo: false
# define the path to the OpenSCAD executable
openscad_path <- "openscad"

# convert stl to png
convert_stl_to_png <- function(stl, png, overwrite = FALSE) {
  if (file.exists(png) && !overwrite) {
    return(list("already done"))
  }
  # openscad rendering options
  # --autocenter and --viewall ensure the model fits the frame
  cmd_args <- c(
    "-o",
    png,
    "--imgsize=1024,1024",
    "--colorscheme=Starnight",
    "--autocenter",
    "--viewall",
    sprintf("-D 'stl=\"%s\"'", stl),
    "png_converter.scad"
  )

  # execute the conversion
  out <- system2(openscad_path, args = cmd_args, stdout = TRUE, stderr = TRUE)
  return(out)
}

# generate png files for all stls
results <-
  tibble::tibble(
    stl = list.files("stl", pattern = "\\.stl$"),
    label = stl |>
      stringr::str_replace("^micrologger_(.*)_nozzle(.*)$", "\\1") |>
      stringr::str_replace_all(stringr::fixed("_"), " ") |>
      stringr::str_to_title(),
    type = stl |>
      stringr::str_replace("^micrologger_([^_]+)(.*)$", "\\1"),
    png = stl |>
      stringr::str_replace("\\.stl$", ".png"),
    result = purrr::map2(
      file.path("stl", stl),
      file.path("png", png),
      convert_stl_to_png
    )
  )
```

```{r}
#| echo: false
#| results: asis
# generate output
results |>
  dplyr::mutate(type = factor(type) |> forcats::fct_relevel("device")) |>
  dplyr::arrange(type) |>
  dplyr::summarise(
    .by = "type",
    code = sprintf("## %s\n\n[![](png/%s)](stl/%s)", label, png, stl) |>
      paste(collapse = "\n\n")
  ) |>
  dplyr::pull(code) |>
  cat(sep = "\n\n")
```

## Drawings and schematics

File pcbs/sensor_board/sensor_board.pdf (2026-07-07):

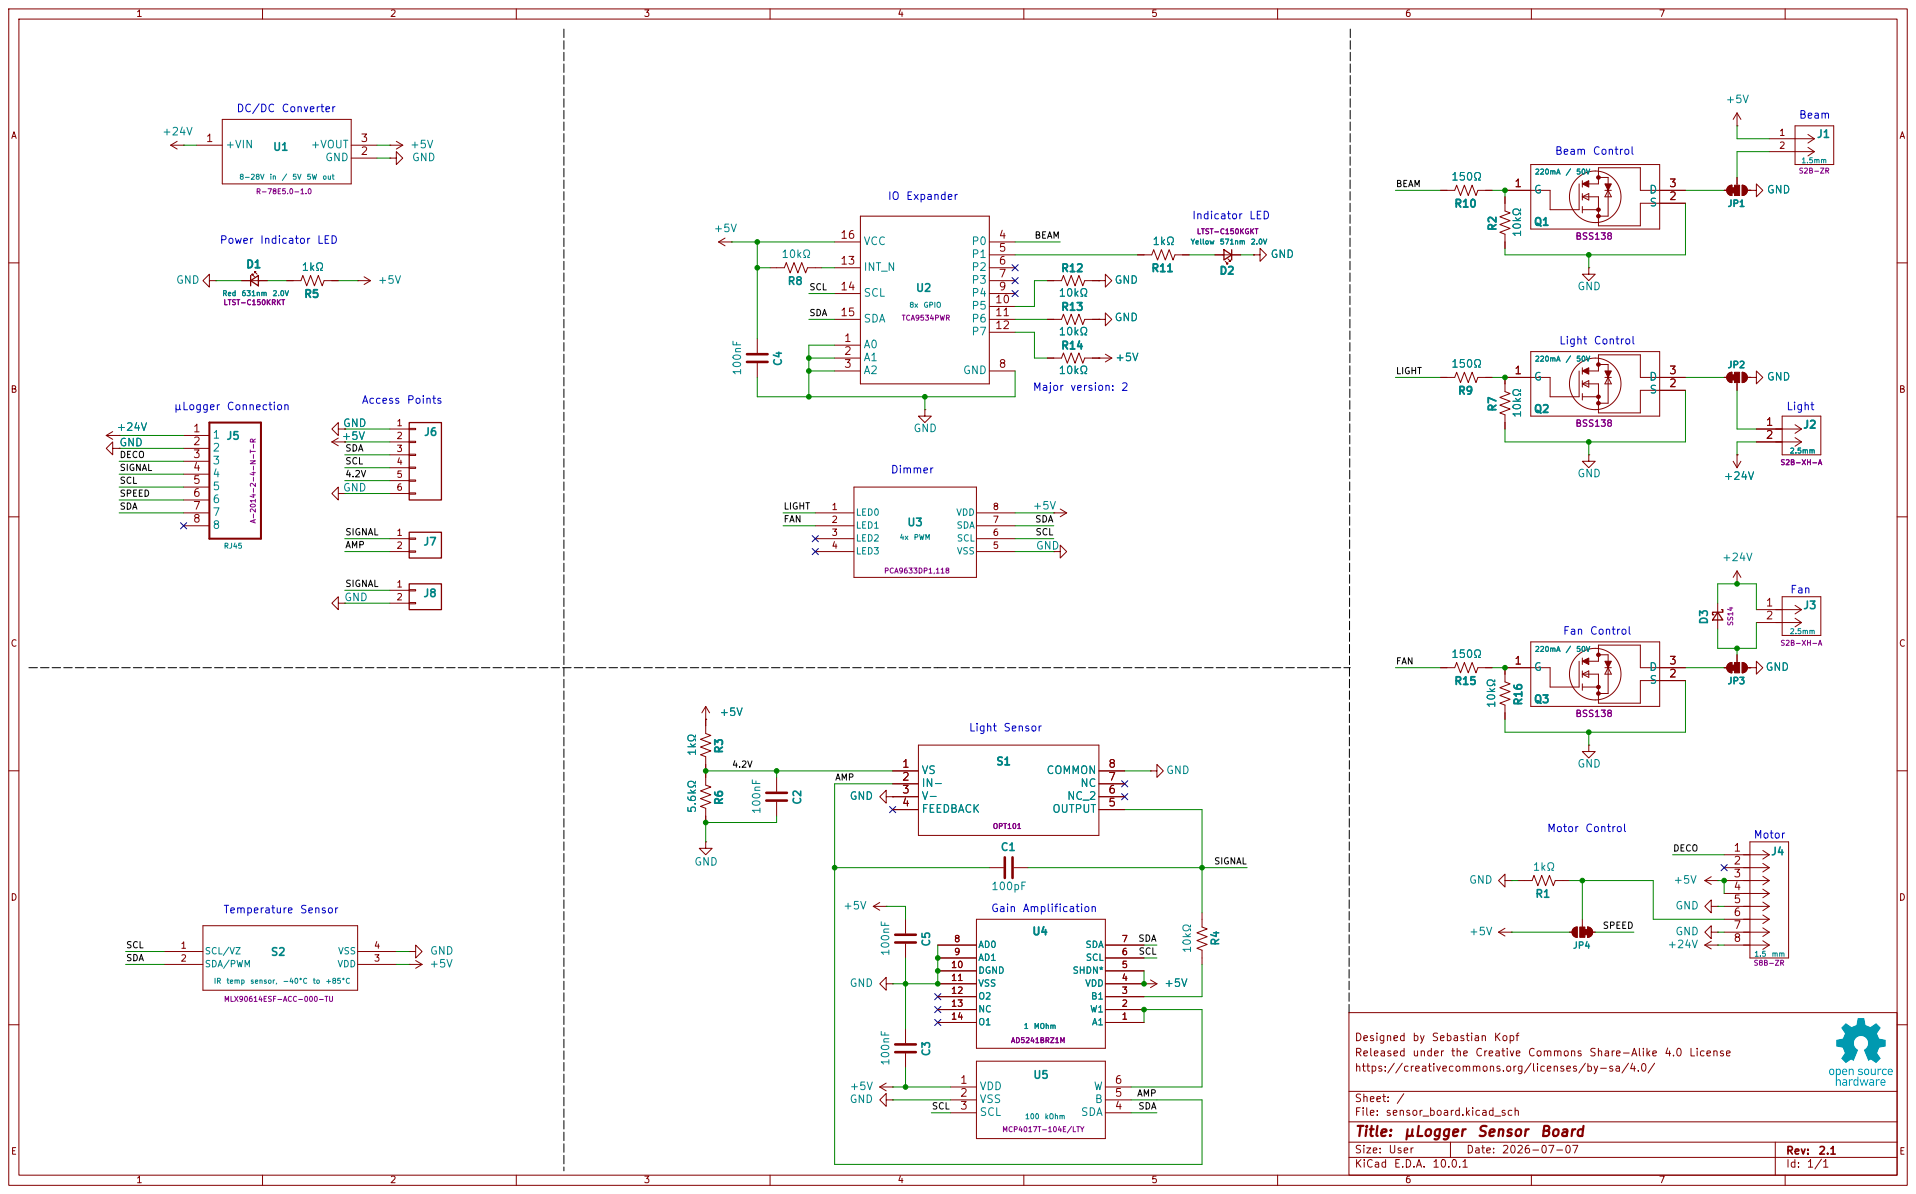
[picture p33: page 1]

GND
SCL SDA SIGNAL DECO

Released under the Creative Commons Share-Alike 4.0 License
https://creativecommons.org/licenses/by-sa/4.0/

Sheet: /
File: sensor_board.kicad_sch
Title: µLogger Sensor Board

Size: User | Rev: 2.1

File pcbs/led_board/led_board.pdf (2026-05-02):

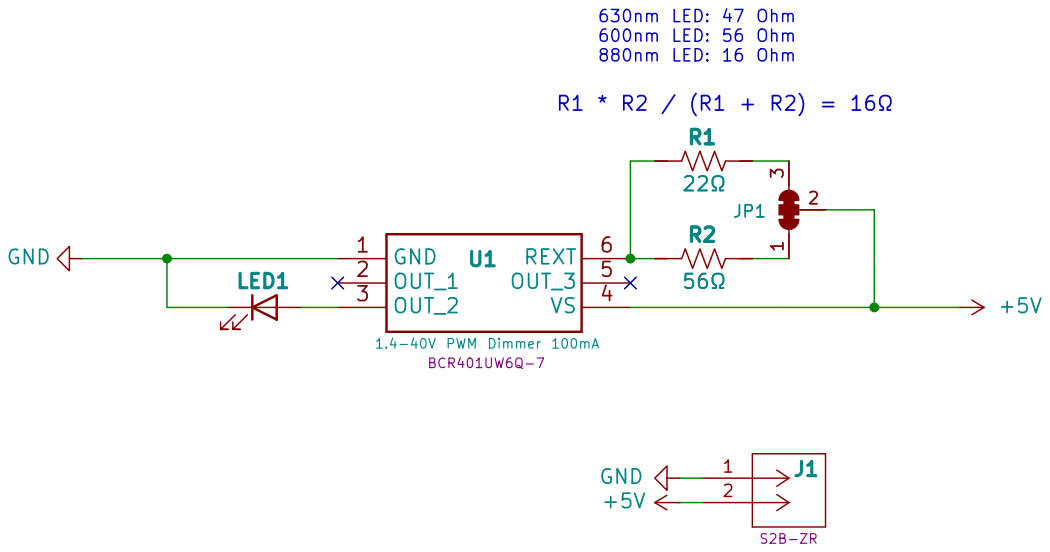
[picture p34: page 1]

Designed by Sebastian Kopf
Released under the Creative Commons Share-Alike 4.0 License
https://creativecommons.org/licenses/by-sa/4.0/

Sheet: /
File: led_board.kicad_sch
Title: µLogger Beam Board

Size: A4 | Rev: 1.1
KiCad E.D.A. 10.0.1 | Id: 1/1

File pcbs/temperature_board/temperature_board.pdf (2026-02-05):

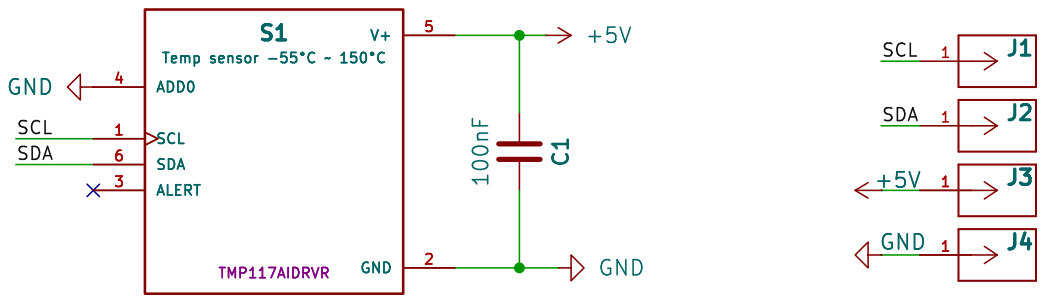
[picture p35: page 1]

Temp sensor þÿ-55°C~ þÿ150°C

Id: 1/1 Title: þÿµLogger Temperature Board

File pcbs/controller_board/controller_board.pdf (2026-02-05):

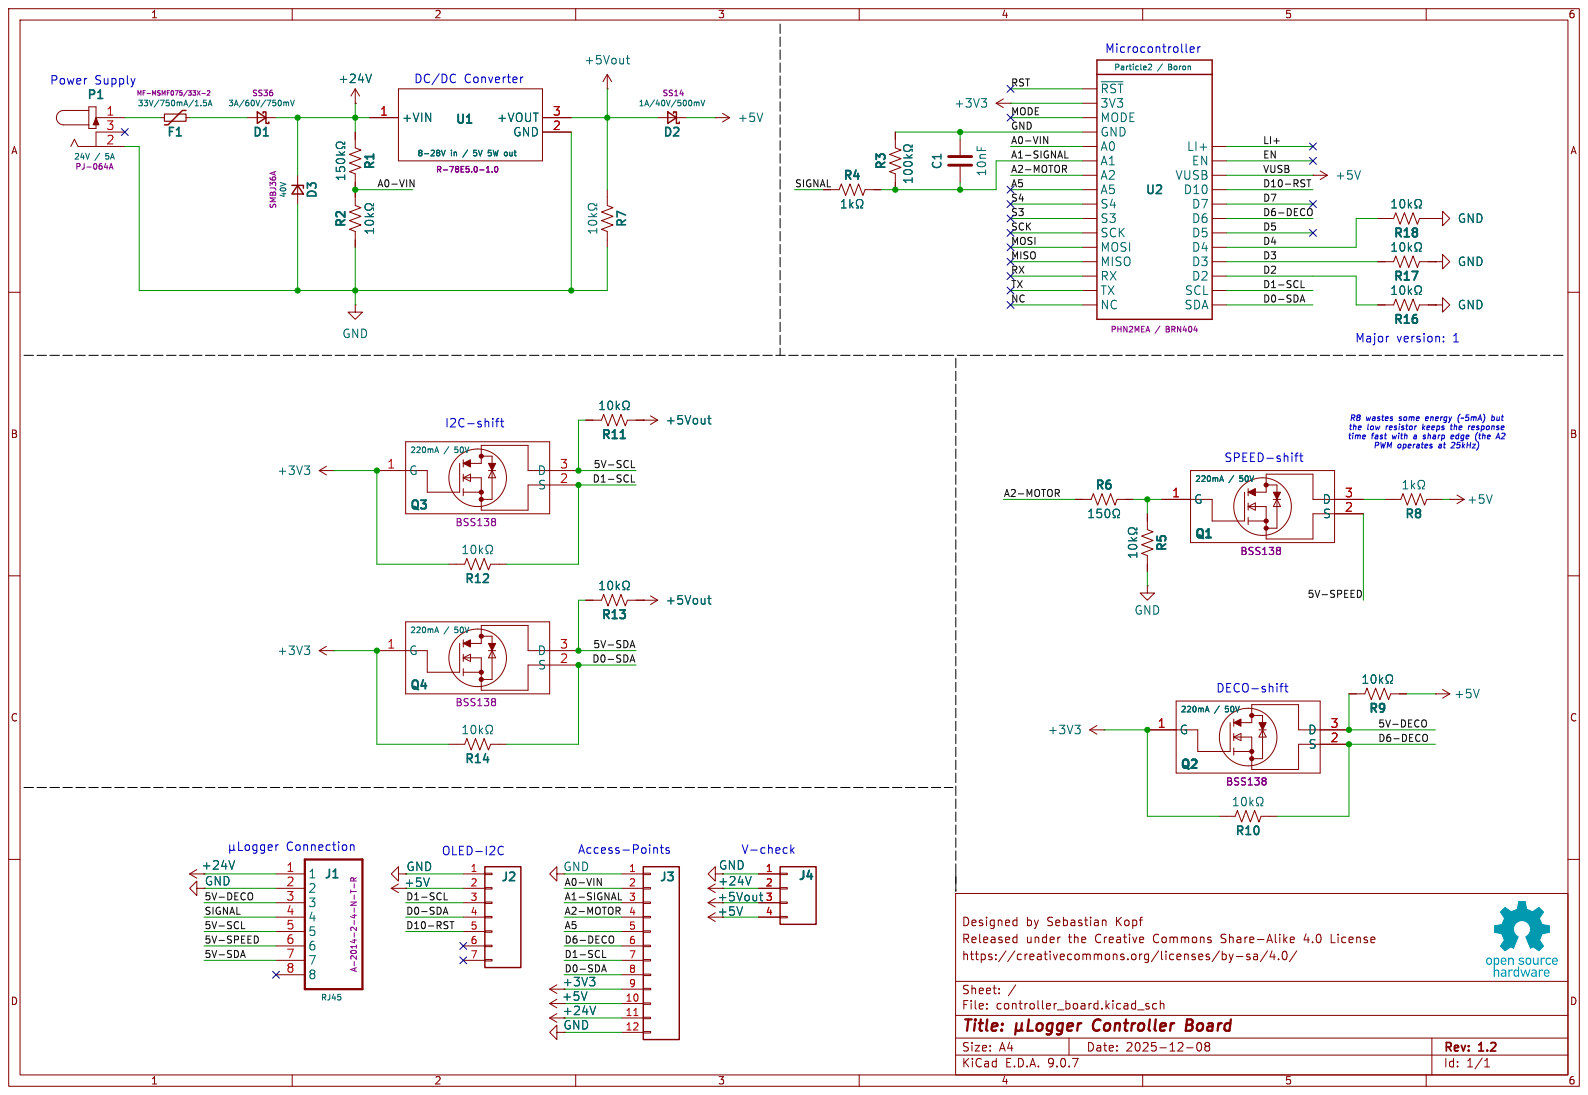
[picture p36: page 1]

the low resistor keeps the response

Id: 1/1 Title: þÿµLogger Controller Board

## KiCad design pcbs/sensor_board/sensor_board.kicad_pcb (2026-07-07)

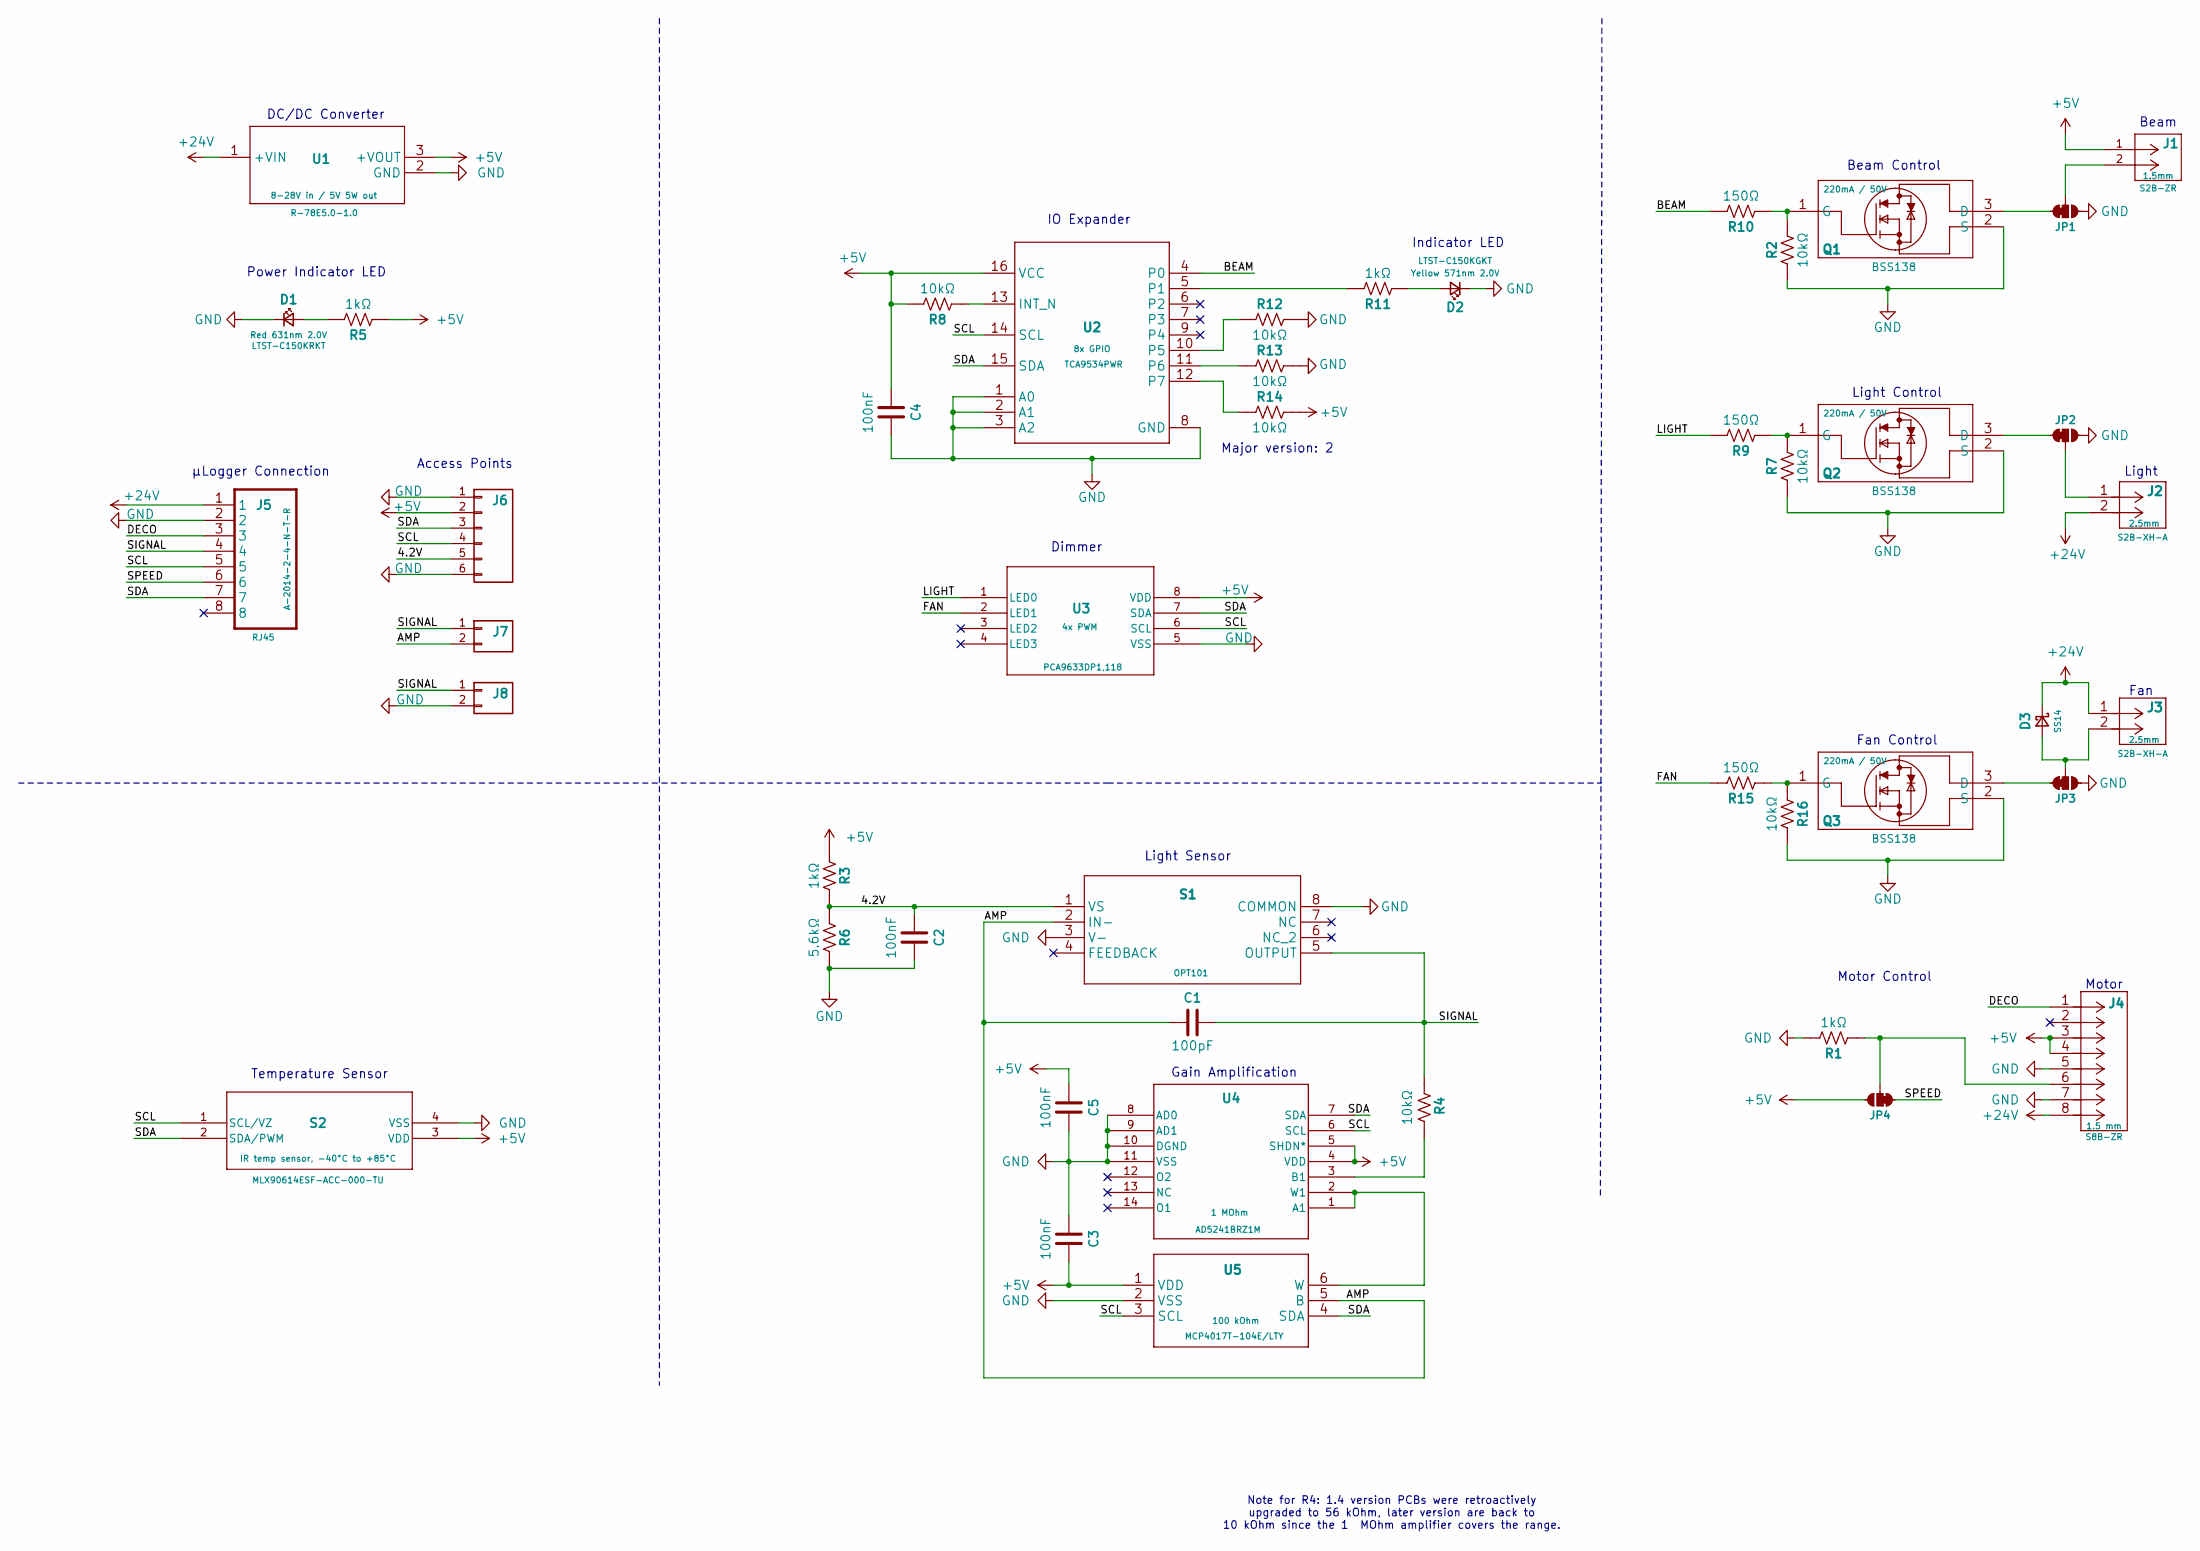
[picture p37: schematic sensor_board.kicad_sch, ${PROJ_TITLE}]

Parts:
C1: 100pF; C_0603; JLCPCB C14858
C2, C4: 100nF; C_0603; JLCPCB C1591
C3, C5: 100nF; C_0603
D1: Red 631nm 2.0V; LED_1206; MPN LTST-C150KRKT; DigiKey 160-1405-1-ND
D2: Yellow 571nm 2.0V; LED_1206; MPN LTST-C150KGKT; DigiKey 160-1404-1-ND
D3: 1A/40V/500mV; D_DO-214AC_SMA; MPN SS14; DigiKey SS14CT-ND
J1: 1.5mm; JST_ZH_2POS_RA; MPN S2B-ZR; DigiKey 455-1669-ND
J2, J3: 2.5mm; JST_XH_2POS_RA; MPN S2B-XH-A; DigiKey 455-S2B-XH-A-ND
J4: 1.5 mm; JST_ZR_8POS_RA; MPN S8B-ZR; DigiKey 455-S8B-ZR-ND
J5: RJ45; RJ45_A-2014-2-4-N-T-R; MPN A-2014-2-4-N-T-R; DigiKey AE10396-ND
J6: Conn_01x06; PIN_HEADERS_1X06
J7, J8: Conn_01x02; PIN_HEADERS_1X02
JP1, JP2, JP3, JP4: Jumper_3_NC-1_Trace
Q1, Q2, Q3: 220mA / 50V; SOT-23-3; MPN BSS138; DigiKey BSS138CT-ND
R1, R5, R11: 1kΩ; R_0603
R2, R7, R12, R13, R14, R16: 10kΩ; R_0603
R3: 1kΩ; R_0603; JLCPCB C118155
R4: 10kΩ; R_1206; JLCPCB C17902
R6: 5.6kΩ; R_0603; JLCPCB C403276
R8: 10kΩ; R_0603; JLCPCB C191124
R9, R15: 150Ω; R_0603
R10: 150Ω; R_0603; JLCPCB C400650
S1: Value; OPT101; MPN OPT101; DigiKey 296-23090-5-ND
S2: IR temp sensor, -40°C to +85°C; MLX90614; MPN MLX90614ESF-ACC-000-TU; DigiKey MLX90614ESF-ACC-000-TU-ND
U1: 8-28V in / 5V 5W out; DC_DC_converter_R-78E5.0-1.0; MPN R-78E5.0-1.0; DigiKey 945-2201-ND
U2: 8x GPIO; SOT-403-1_TSSOP16; MPN TCA9534PWR; DigiKey 296-40574-1-ND
U3: 4x PWM; SOT-505-1_TSSOP8; MPN PCA9633DP1,118; DigiKey 568-3236-1-ND
U4: 1 MOhm; 14-SOIC; MPN AD5241BRZ1M; DigiKey 505-AD5241BRZ1M-ND
U5: 100 kOhm; SOT-363_TSSOP6_SC88; MPN MCP4017T-104E/LTY; DigiKey 150-MCP4017T-104E/LTYCT-ND

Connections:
+5V: C3.2, C4.1, C5.1, J1.1, J4.3, J4.4, J6.2, JP4.3 (C), R3.1, R5.1, R8.2, R14.2, S2.3 (VDD), U1.3 (+VOUT), U2.16 (VCC), U3.8 (VDD), U4.4 (VDD), U4.5 (SHDN*), U5.1 (VDD)
+24V: D3.1 (K), J2.2, J3.1, J4.8, J5.1, U1.1 (+VIN)
/4.2V: C2.1, J6.5, R3.2, R6.1, S1.1 (VS)
/AMP: C1.1, J7.2, S1.2 (IN-), U5.5 (B)
/BEAM: R10.2, U2.4 (P0)
/DECO: J4.1, J5.3
/FAN: R15.2, U3.2 (LED1)
/LIGHT: R9.2, U3.1 (LED0)
/SCL: J5.5, J6.4, S2.1 (SCL/VZ), U2.14 (SCL), U3.6 (SCL), U4.6 (SCL), U5.3 (SCL)
/SDA: J5.7, J6.3, S2.2 (SDA/PWM), U2.15 (SDA), U3.7 (SDA), U4.7 (SDA), U5.4 (SDA)
/SIGNAL: C1.2, J5.4, J7.1, J8.1, R4.1, S1.5 (OUTPUT)
/SPEED: J5.6, JP4.1 (A)
GND: C2.2, C3.1, C4.2, C5.2, D1.1 (K), D2.1 (K), J4.5, J4.7, J5.2, J6.1, J6.6, J8.2, JP1.3 (C), JP2.3 (C), JP3.3 (C), Q1.2 (S), Q2.2 (S), Q3.2 (S), R1.2, R2.1, R6.2, R7.1, R12.2, R13.2, R16.2, S1.3 (V-), S1.8 (COMMON), S2.4 (VSS), U1.2 (GND), U2.1 (A0), U2.2 (A1), U2.3 (A2), U2.8 (GND), U3.5 (VSS), U4.8 (AD0), U4.9 (AD1), U4.10 (DGND), U4.11 (VSS), U5.2 (VSS)
unnamed: D1.2 (A), R5.2
unnamed: D2.2 (A), R11.1
unnamed: D3.2 (A), J3.2, JP3.2 (B)
unnamed: JP1.1 (A), Q1.3 (D)
unnamed: J1.2, JP1.2 (B)
unnamed: JP2.1 (A), Q2.3 (D)
unnamed: J2.1, JP2.2 (B)
unnamed: JP3.1 (A), Q3.3 (D)
unnamed: J4.6, JP4.2 (B), R1.1
unnamed: Q1.1 (G), R2.2, R10.1
unnamed: Q2.1 (G), R7.2, R9.1
unnamed: Q3.1 (G), R15.1, R16.1
unnamed: R8.1, U2.13 (INT_N)
unnamed: R11.2, U2.5 (P1)
unnamed: R12.1, U2.10 (P5)
unnamed: R13.1, U2.11 (P6)
unnamed: R14.1, U2.12 (P7)
unnamed: U4.1 (A1), U4.2 (W1), U5.6 (W)
unnamed: R4.2, U4.3 (B1)

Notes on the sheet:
Light Sensor
Fan Control
Note for R4: 1.4 version PCBs were retroactively upgraded to 56 kOhm, later version are back to 10 kOhm since the 1 MOhm amplifier covers the range.
Gain Amplification
IO Expander
Motor Control
Light Control
Light
Access Points
Dimmer
Fan
DC/DC Converter
Beam Control
Motor
Temperature Sensor
Indicator LED
µLogger Connection
Power Indicator LED
Beam
Major version: 2

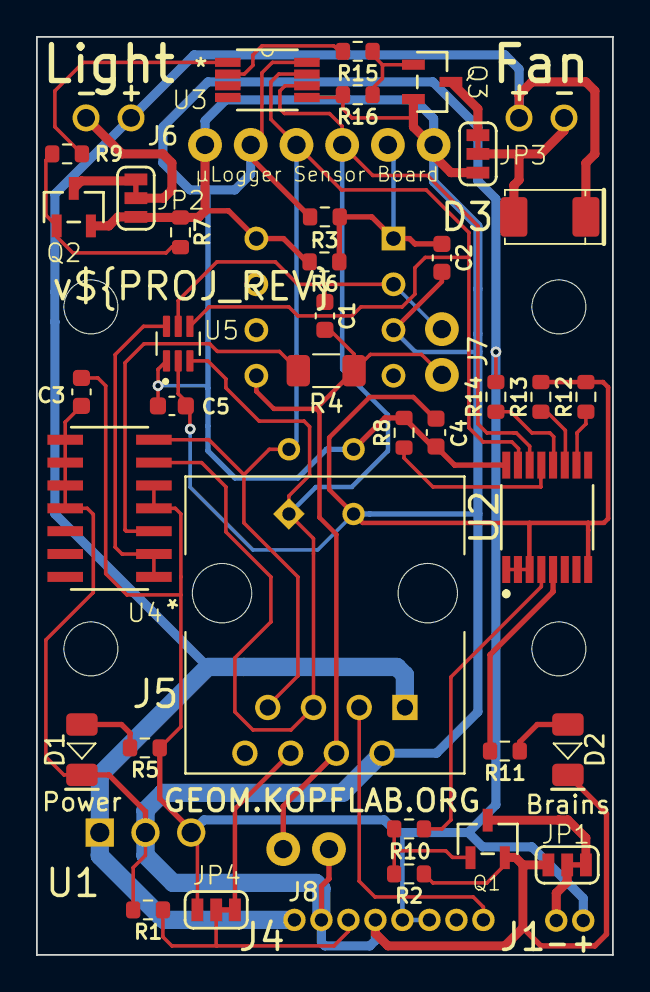
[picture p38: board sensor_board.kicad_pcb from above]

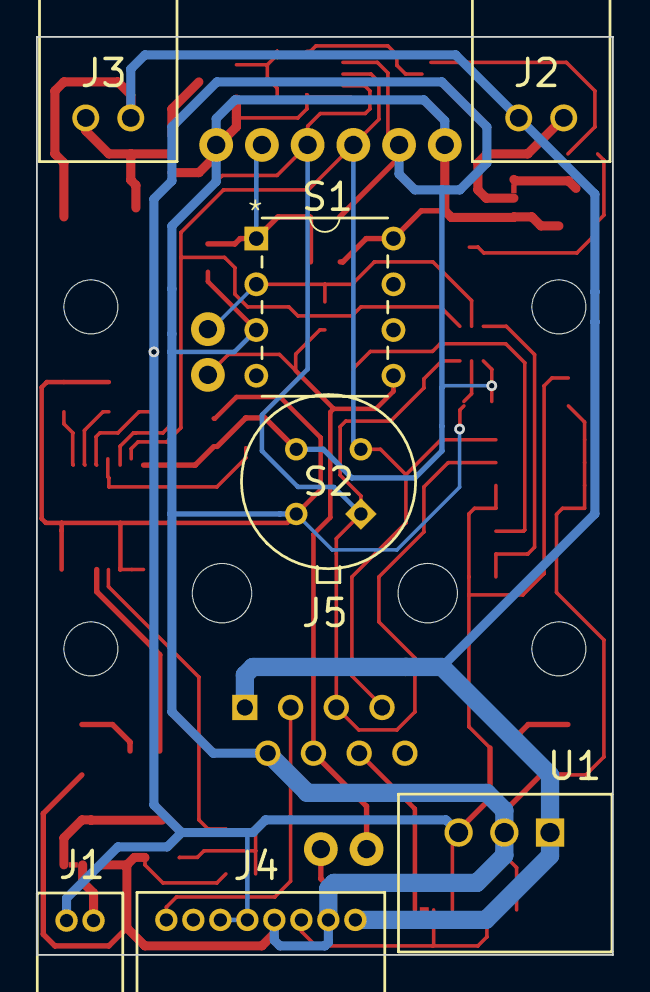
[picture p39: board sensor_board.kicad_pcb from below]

Board: 2 copper layers, 32.0 x 51.0 mm, 46 parts (7 on the bottom side), 32 nets.

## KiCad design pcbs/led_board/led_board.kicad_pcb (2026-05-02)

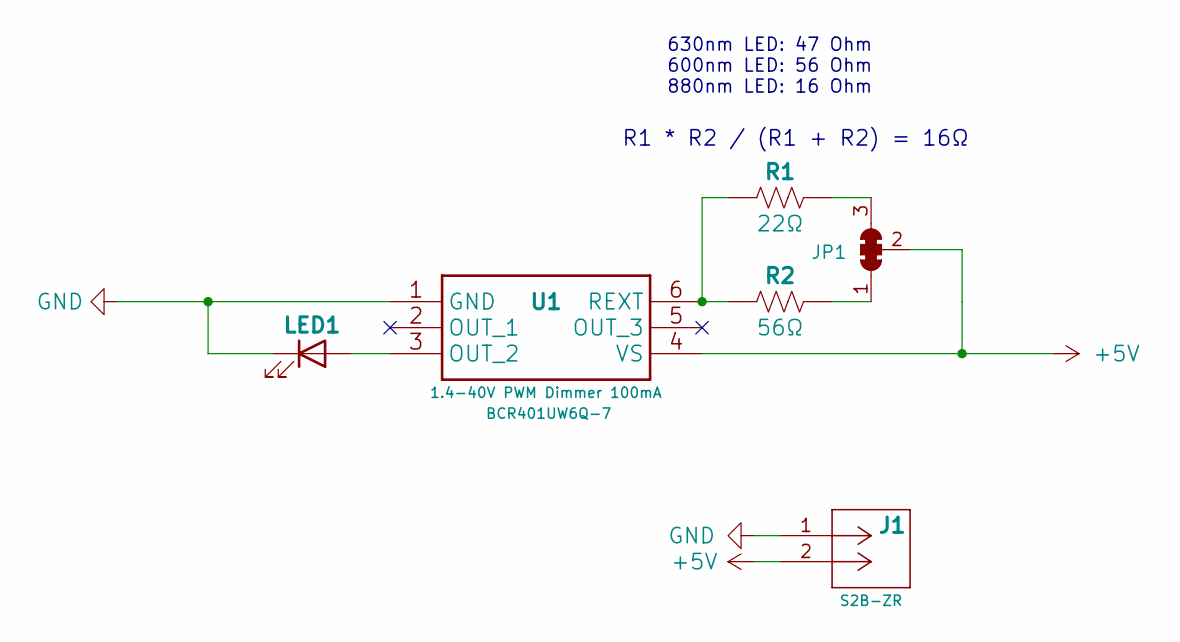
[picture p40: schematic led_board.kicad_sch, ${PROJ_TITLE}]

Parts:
J1: CONN HEADER R/A 2POS 1.5MM; JST_ZH_2POS_RA; MPN S2B-ZR; DigiKey 455-1669-ND
JP1: SolderJumper_3_Bridged123; SolderJumper3_Bridged
LED1: 630nm 1.9V 50mA; TO-46-2; MPN MTE7063NK2-UR; DigiKey 1125-1382-ND
R1: 22Ω; R_1206; JLCPCB C17958
R2: 56Ω; R_1206; JLCPCB C17995
U1: 1.4-40V PWM Dimmer 100mA; SOT-23-6; MPN BCR401UW6Q-7; DigiKey BCR401UW6Q-7DICT-ND

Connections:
+5V: J1.2, JP1.2 (C), U1.4 (VS)
GND: J1.1, LED1.1 (K), U1.1 (GND)
unnamed: JP1.1 (A), R2.2
unnamed: JP1.3 (B), R1.2
unnamed: LED1.2 (A), U1.3 (OUT_2)
unnamed: R1.1, R2.1, U1.6 (REXT)

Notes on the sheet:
R1 * R2 / (R1 + R2) = 16Ω
630nm LED: 47 Ohm 600nm LED: 56 Ohm 880nm LED: 16 Ohm

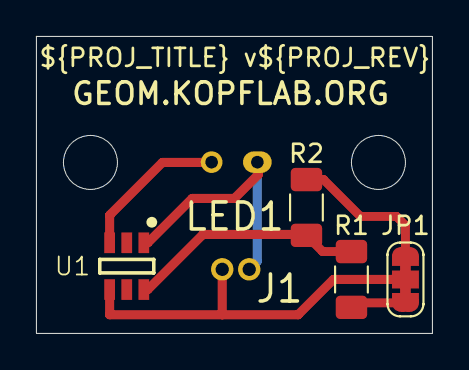
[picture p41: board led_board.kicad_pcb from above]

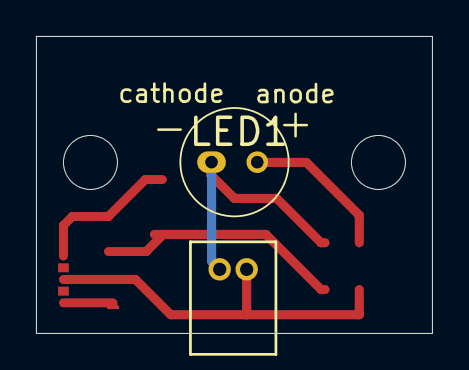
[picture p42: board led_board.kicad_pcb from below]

Board: 2 copper layers, 22.0 x 16.5 mm, 6 parts (2 on the bottom side), 6 nets.

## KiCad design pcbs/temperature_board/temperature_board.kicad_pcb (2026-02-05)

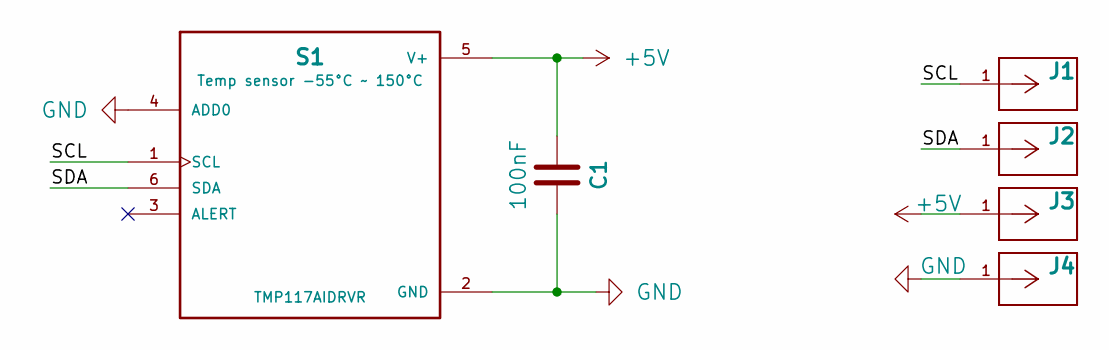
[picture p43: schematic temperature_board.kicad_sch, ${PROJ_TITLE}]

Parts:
C1: 100nF; C_0603; JLCPCB C1591
J1: SCL; PIN_HEADERS_1X01
J2: SDA; PIN_HEADERS_1X01
J3: +5V; PIN_HEADERS_1X01
J4: GND; PIN_HEADERS_1X01
S1: Temp sensor -55°C ~ 150°C; WSON-6_2x2mm_nopad; MPN TMP117AIDRVR; DigiKey 296-51834-1-ND

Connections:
+5V: C1.1, J3.1, S1.5 (V+)
/SCL: J1.1, S1.1 (SCL)
/SDA: J2.1, S1.6 (SDA)
GND: C1.2, J4.1, S1.2 (GND), S1.4 (ADD0)

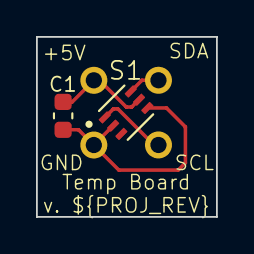
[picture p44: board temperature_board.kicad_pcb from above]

Board: 2 copper layers, 10.0 x 10.0 mm, 6 parts (0 on the bottom side), 4 nets.

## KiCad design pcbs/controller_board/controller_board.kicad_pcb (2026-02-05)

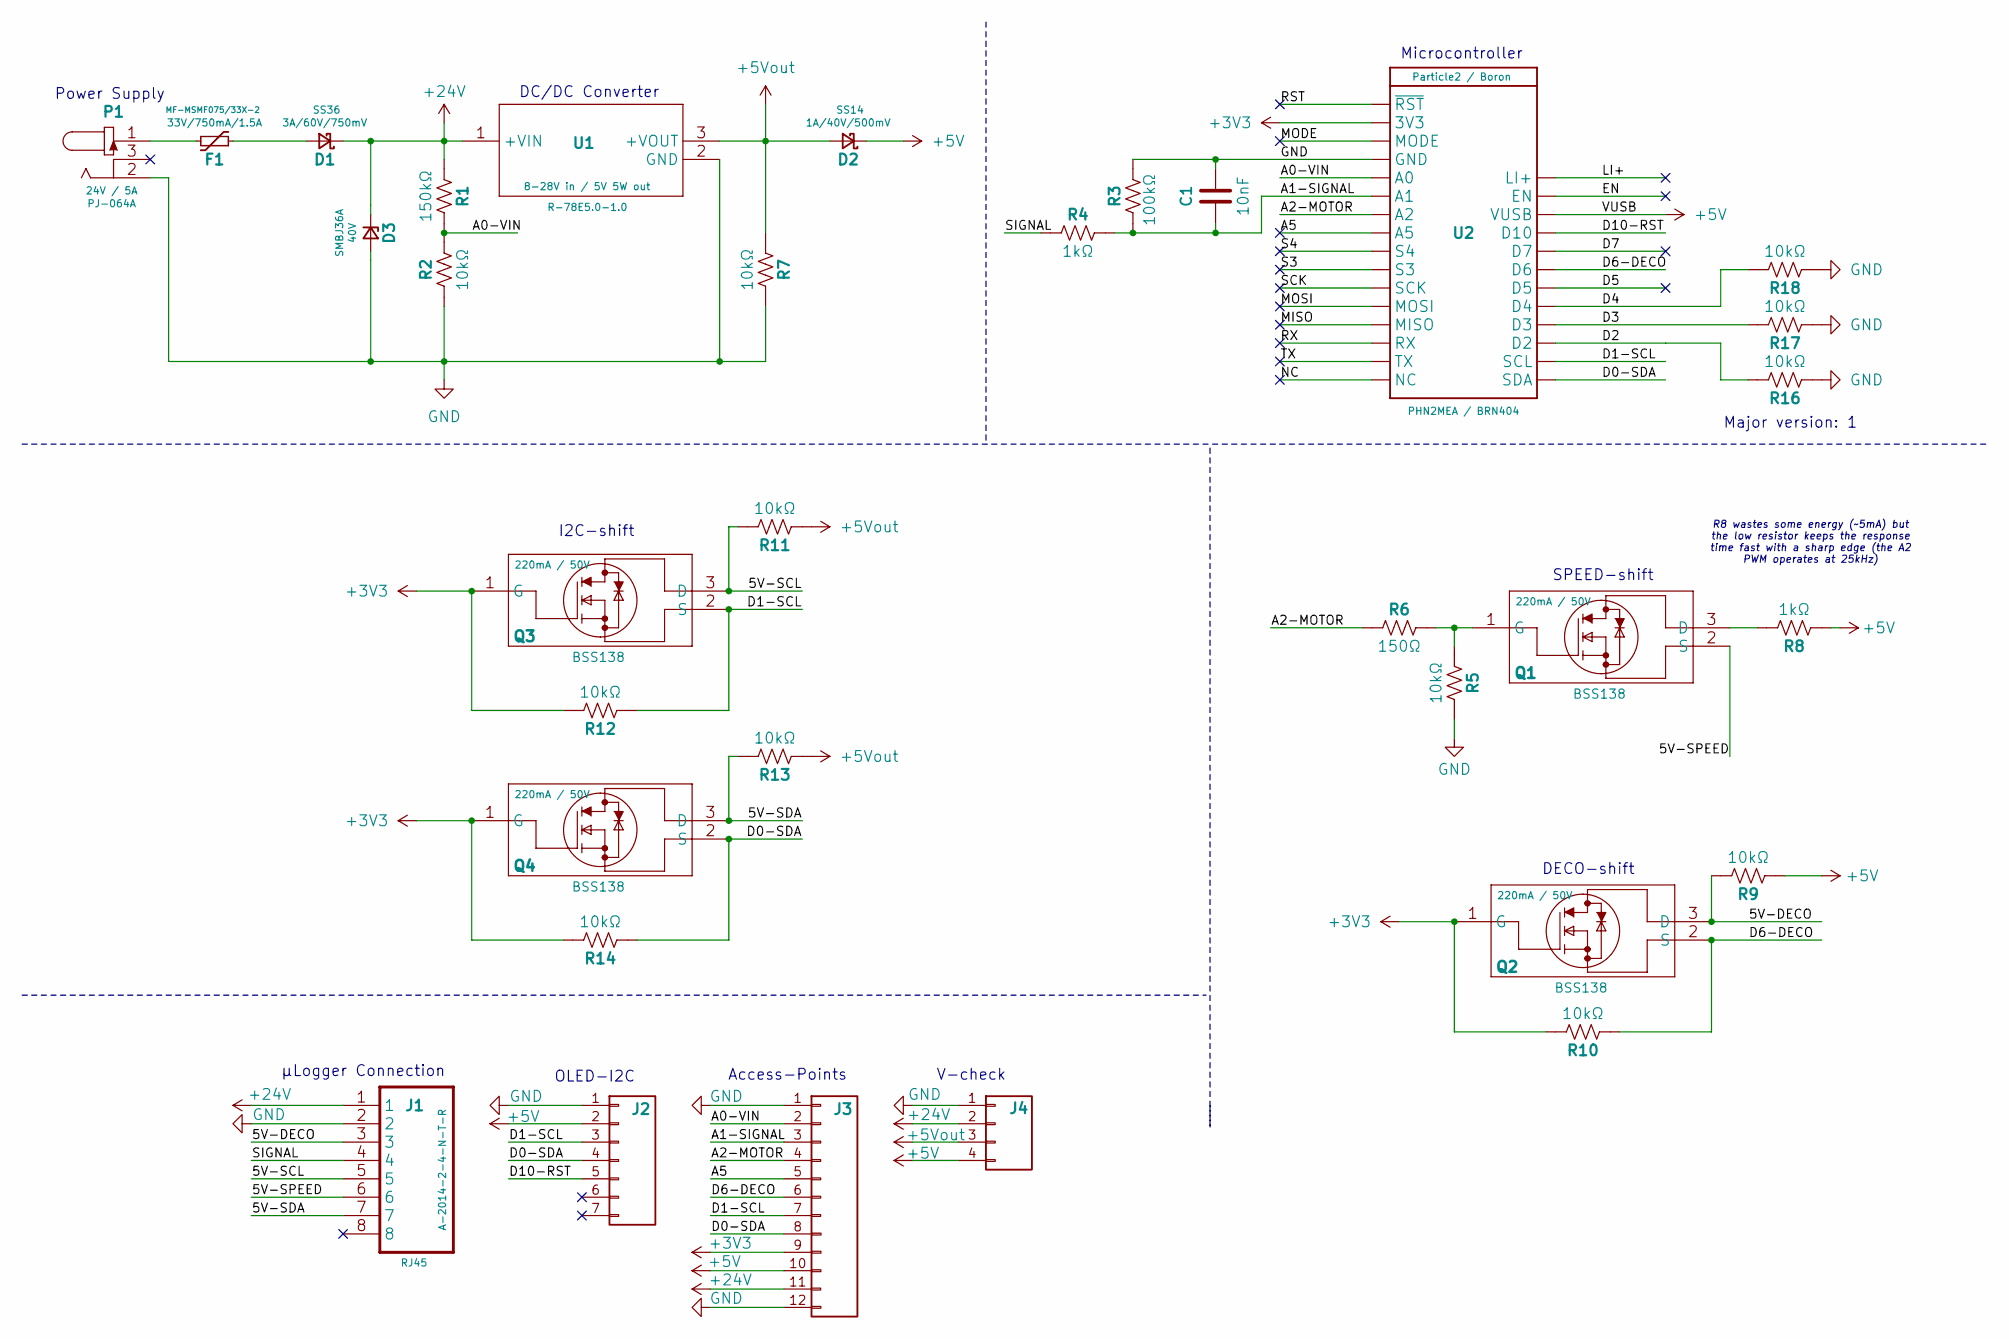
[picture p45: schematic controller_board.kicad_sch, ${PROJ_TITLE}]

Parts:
C1: 10nF; C_0603; JLCPCB C1589
D1: 3A/60V/750mV; D_DO-214AB_SMC; MPN SS36; DigiKey SS36FSCT-ND
D2: 1A/40V/500mV; D_DO-214AC_SMA; MPN SS14; DigiKey SS14CT-ND
D3: 40V; D_DO-214AA_SMB; MPN SMBJ36A; DigiKey SMBJ36ALFCT-ND
F1: 33V/750mA/1.5A; Fuse_1812; MPN MF-MSMF075/33X-2; DigiKey 118-MF-MSMF075/33X-2CT-ND
J1: RJ45; RJ45_A-2014-2-4-N-T-R; MPN A-2014-2-4-N-T-R; DigiKey AE10396-ND
J2: Conn_01x07; PIN_HEADERS_1X07
J3: Conn_01x12; PIN_HEADERS_1X12
J4: PINHD-1X4; PIN_HEADERS_1X04
P1: 24V / 5A; PWR_JACK_PJ-064A; MPN PJ-064A; DigiKey CP-064A-ND
Q1, Q2, Q3, Q4: 220mA / 50V; SOT-23-3; MPN BSS138; DigiKey BSS138CT-ND
R1: 150kΩ; R_1206; JLCPCB C17916
R2, R7, R9, R10, R11, R12, R13, R14, R16, R17, R18: 10kΩ; R_1206
R3: 100kΩ; R_1206; JLCPCB C17900
R4: 1kΩ; R_1206
R5: 10kΩ; R_1206; JLCPCB C17902
R6: 150Ω; R_1206; JLCPCB C17917
R8: 1kΩ; R_1206; JLCPCB C4410
U1: 8-28V in / 5V 5W out; DC_DC_converter_R-78E5.0-1.0; MPN R-78E5.0-1.0; DigiKey 945-2201-ND
U2: Particle2 / Boron; PHOTON2; MPN PHN2MEA / BRN404

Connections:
+3V3: J3.9, Q2.1 (G), Q3.1 (G), Q4.1 (G), R10.2, R12.2, R14.2, U2.2 (3V3)
+5V: D2.1 (K), J2.2, J3.10, J4.4, R8.1, R9.1, U2.26 (VUSB)
+5Vout: D2.2 (A), J4.3, R7.1, R11.1, R13.1, U1.3 (+VOUT)
+24V: D1.1 (K), D3.1 (K), J1.1, J3.11, J4.2, R1.1, U1.1 (+VIN)
/5V-DECO: J1.3, Q2.3 (D), R9.2
/5V-SCL: J1.5, Q3.3 (D), R11.2
/5V-SDA: J1.7, Q4.3 (D), R13.2
/5V-SPEED: J1.6, Q1.2 (S)
/A0-VIN: J3.2, R1.2, R2.2, U2.5 (A0)
/A1-SIGNAL: C1.1, J3.3, R3.1, R4.2, U2.6 (A1)
/A2-MOTOR: J3.4, R6.1, U2.7 (A2)
/A5: J3.5, U2.8 (A5)
/D0-SDA: J2.4, J3.8, Q4.2 (S), R14.1, U2.17 (SDA)
/D1-SCL: J2.3, J3.7, Q3.2 (S), R12.1, U2.18 (SCL)
/D2: R16.2, U2.19 (D2)
/D3: R17.2, U2.20 (D3)
/D4: R18.2, U2.21 (D4)
/D5: U2.22 (D5)
/D6-DECO: J3.6, Q2.2 (S), R10.1, U2.23 (D6)
/D7: U2.24 (D7)
/D10-RST: J2.5, U2.25 (D10)
/EN: U2.27 (EN)
/LI+: U2.28 (LI+)
/MISO: U2.13 (MISO)
/MODE: U2.3 (MODE)
/MOSI: U2.12 (MOSI)
/NC: U2.16 (NC)
/RST: U2.1 (~RST)
/RX: U2.14 (RX)
/S3: U2.10 (S3)
/S4: U2.9 (S4)
/SCK: U2.11 (SCK)
/SIGNAL: J1.4, R4.1
/TX: U2.15 (TX)
GND: C1.2, D3.2 (A), J1.2, J2.1, J3.1, J3.12, J4.1, P1.2, R2.1, R3.2, R5.2, R7.2, R16.1, R17.1, R18.1, U1.2 (GND), U2.4 (GND)
unnamed: D1.2 (A), F1.1
unnamed: F1.2, P1.1
unnamed: Q1.3 (D), R8.2
unnamed: Q1.1 (G), R5.1, R6.2

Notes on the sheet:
Major version: 1
µLogger Connection
Microcontroller
R8 wastes some energy (~5mA) but the low resistor keeps the response time fast with a sharp edge (the A2 PWM operates at 25kHz)
SPEED-shift
Power Supply
DC/DC Converter
Access-Points
V-check
DECO-shift
I2C-shift
OLED-I2C

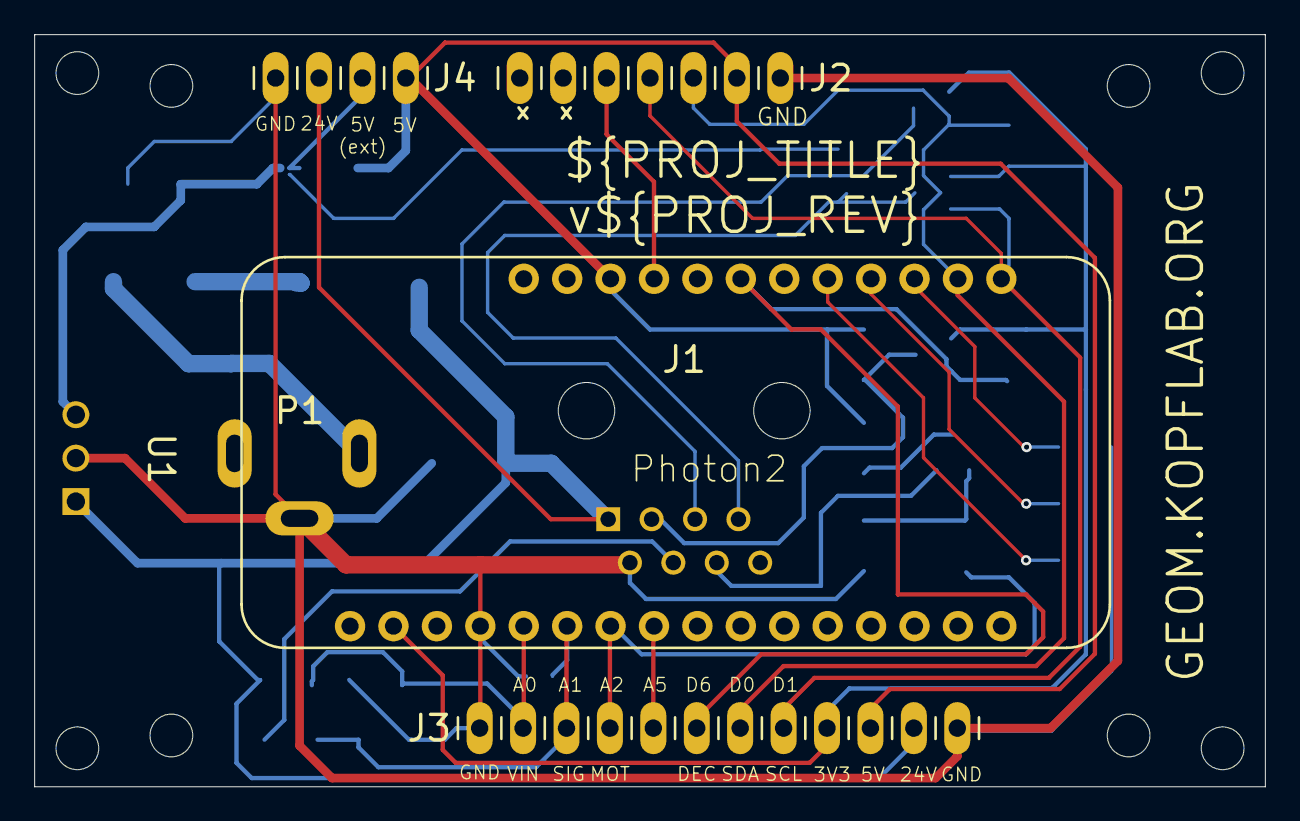
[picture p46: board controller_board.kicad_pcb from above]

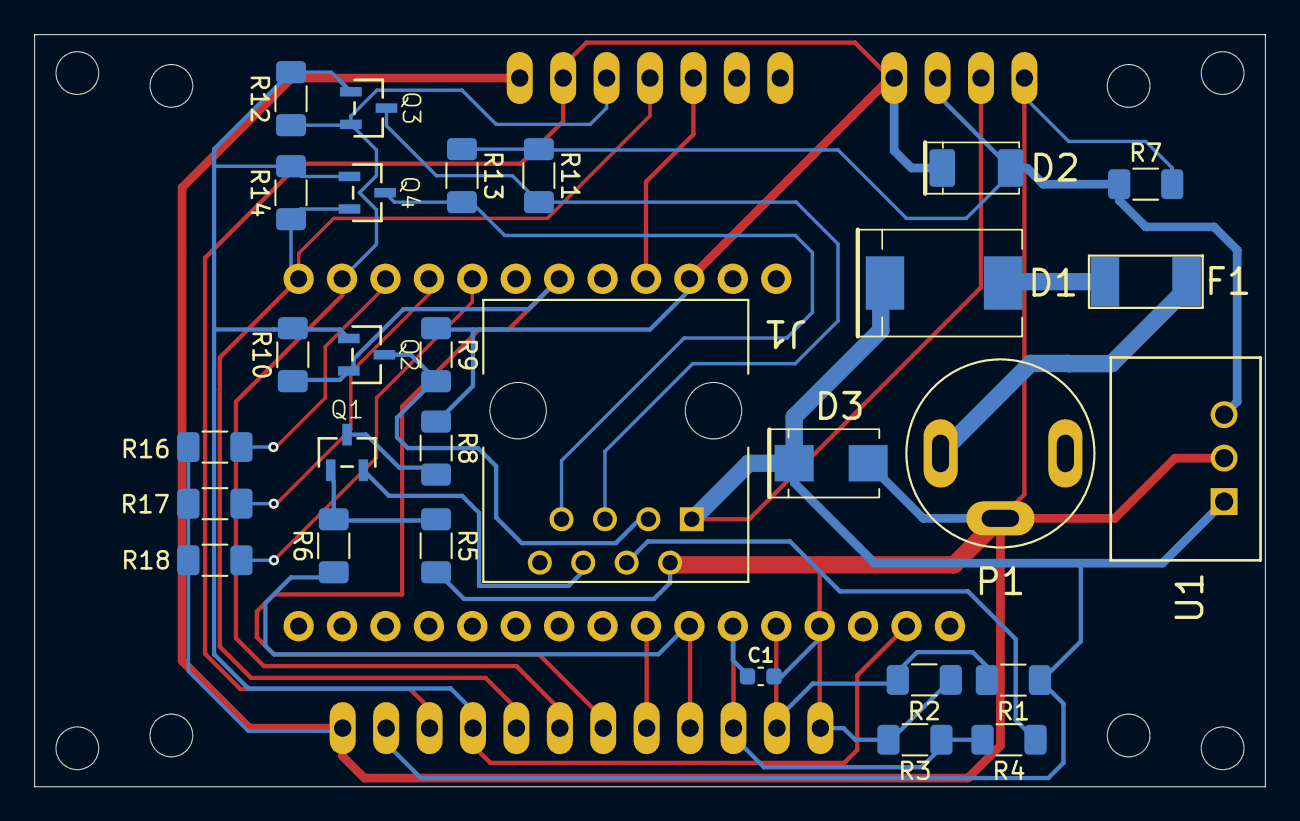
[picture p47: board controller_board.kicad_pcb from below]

Board: 2 copper layers, 72.0 x 44.0 mm, 41 parts (29 on the bottom side), 25 nets.

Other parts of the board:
H1, H2, H3, H4, H5, H6, H7, H8: MountingHole_2.5mm_M2.5

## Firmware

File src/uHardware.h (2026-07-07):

#pragma once

#include "uTypedef.h"
#include "enums.h"
#include "uMultask.h"
#ifdef SDDS_ON_PARTICLE
#include "uParticleSystem.h"
#endif

// hardware parts
#include "uHardwareMotorNidec24H.h"
#include "uHardwareIOExpanderTCA9534.h"
#include "uHardwareRheostatMCP4017.h"
#include "uHardwareRheostatAD5246.h"
#include "uHardwareRheostatAD5241.h"
#include "uHardwarePwmPCA9633.h"
#include "uHardwareSensorOPT101.h"
#include "uHardwareSensorTMP117.h"
#include "uHardwareSensorVoltage.h"
#include "uHardwareDisplay.h"

// hardware constants
#define MICROLOGGER_VOLTAGE_PIN A0
#define MICROLOGGER_VOLTAGE_DIVIDER_REF 3.3
#define MICROLOGGER_VOLTAGE_DIVIDER_R1 150.0
#define MICROLOGGER_VOLTAGE_DIVIDER_R2 10.0
#define MICROLOGGER_VOLTAGE_SCHOTTKY_DROP 0.5
#define MICROLOGGER_SIGNAL_PIN A1
#define MICROLOGGER_SPEED_PIN A2
#define MICROLOGGER_DECODER_PIN D6
#define MICROLOGGER_CONTROLLER_VERSION_PIN1 D2
#define MICROLOGGER_CONTROLLER_VERSION_PIN2 D3
#define MICROLOGGER_CONTROLLER_VERSION_PIN3 D4

/**
 * @brief hardware handler
 * uses a TmenuHandle for the convenience of sdds_vars but is not usually
 * included in the tree except for stand-alone testing
 */
class Thardware : public TmenuHandle
{

public:
    // enumerations
    using Ti2cAction = ThardwareI2C::Taction;
    using Ti2cError = ThardwareI2C::Terror;

    using TioMode = ThardwareIOExpander::Tmode;
    using TioValue = ThardwareIOExpander::Tvalue;

    using TbeamState = ThardwareIOExpander::Tmode;
    using TbeamValue = ThardwareIOExpander::Tvalue;
    using TlightValue = ThardwarePwmPCA9633::Tvalue;
    using TfanValue = ThardwarePwmPCA9633::Tvalue;

    using TmotorError = ThardwareMotorNidec24H::Terror;
    using TsignalError = ThardwareSensorOPT101::Terror;

private:
    // in case it is used in a tree
    Tmeta meta() override { return Tmeta{TYPE_ID, 0, "HARDWARE"}; }

    // get the version of the sensor board
    uint8_t getSensorBoardVersion()
    {
        expander.pin6 = TioMode::INPUT;
        expander.pin7 = TioMode::INPUT;
        expander.pin8 = TioMode::INPUT;
        expander.action = Ti2cAction::read;
        if (expander.error == Ti2cError::none)
        {
            uint8_t b0 = expander.value8 == TioValue::HIGH ? 1 : 0;
            uint8_t b1 = expander.value7 == TioValue::HIGH ? 1 : 0;
            uint8_t b2 = expander.value6 == TioValue::HIGH ? 1 : 0;
            uint8_t version = (b2 << 2) | (b1 << 1) | b0;
            return version + 1;
        }
        // error
        return 0;
    }

    // gain dpot helpers ------------------------------------------------------------------
    // The secondary gain dpot depends on the sensor board version: dpot2 (AD5246, 100 kOhm)
    // on v1, dpot3 (AD5241, 1 MOhm) on v2. Until the version is known (before the expander
    // connects) we default to the v1 layout.

    // is the 1 MOhm dpot3 (AD5241) the available secondary gain pot on this sensor board? yes, starting at sensor PCB version 2
    bool hasHighGainDpot() { return pcbVersions.sensor >= 2; }

    // total resistance the gain dpots can add on top of the base resistance
    dtypes::uint32 dpotMaxResistance_Ohm()
    {
        return dpot1.maxResistance_Ohm + (hasHighGainDpot() ? dpot3.maxResistance_Ohm : dpot2.maxResistance_Ohm);
    }

    // maximum number of gain steps. Steps are always counted in fine (dpot1-sized) units so
    // the scale stays uniform and monotonic regardless of the secondary pot's step size.
    dtypes::uint16 maxGainSteps()
    {
        if (hasHighGainDpot())
            // dpot3 (1 MOhm) + dpot1 (100 kOhm) expressed in dpot1-sized steps
            return static_cast<dtypes::uint16>(round(static_cast<double>(dpotMaxResistance_Ohm()) * dpot1.maxSteps / dpot1.maxResistance_Ohm));
        else
            // two equal 100 kOhm pots in series (they share one midpoint step)
            return dpot1.maxSteps + dpot2.maxSteps - 1;
    }

public:
    // pcb versions
    class Tpcbs : public TmenuHandle
    {
    public:
        sdds_var(Tuint8, controller, sdds::opt::readonly);
        sdds_var(Tuint8, sensor, sdds::opt::readonly);
    };
    sdds_var(Tpcbs, pcbVersions);
    // display and io expander
    sdds_var(ThardwareDisplay, display);
    sdds_var(ThardwareIOExpander, expander);
    // digital pots
    // dpot1 (MCP4017, 100 kOhm) is present on every sensor board; the secondary gain pot
    // depends on the sensor board version: dpot2 (AD5246, 100 kOhm) on v1, dpot3 (AD5241,
    // 1 MOhm) on v2. Only the one populated on the connected board is ever sent I2C commands.
    sdds_var(ThardwareRheostatMCP4017, dpot1);
    sdds_var(ThardwareRheostatAD5246, dpot2);
    sdds_var(ThardwareRheostatAD5241, dpot3);
    // overall gain
    class Tgain : public TmenuHandle
    {
    public:
        sdds_var(Tuint32, base_Ohm, sdds::opt::saveval, 10000); // base resistance in the amplification circuit, sensor board version 2+
        sdds_var(Tuint16, steps);                               // gain steps
        sdds_var(Tuint32, total_Ohm, sdds::opt::readonly);      // total gain of the amplifier circuit
        sdds_var(Ti2cError, error, sdds::opt::readonly);        // i2c error
    };
    sdds_var(Tgain, gain);
    // signals
    sdds_var(ThardwareSensorOPT101, signal);
    sdds_var(ThardwareSensorTMP117, temperature);
    sdds_var(ThardwareSensorVoltage, voltage);
    // dimmer and motor
    sdds_var(ThardwarePwmPCA9633, dimmer);
    sdds_var(ThardwareMotorNidec24H, motor);

    // aliases
    decltype(expander.pin2) &i2cState = expander.pin2;
    decltype(expander.value2) &i2cValue = expander.value2;

    decltype(expander.error) &beamError = expander.error;
    decltype(expander.action) &beamAction = expander.action;
    decltype(expander.pin1) &beamState = expander.pin1;
    decltype(expander.value1) &beamValue = expander.value1;

    decltype(dimmer.action) &fanLightAction = dimmer.action;
    decltype(dimmer.error) &fanLightError = dimmer.error;
    decltype(dimmer.status) &fanLightStatus = dimmer.status;

    decltype(dimmer.state1) &lightState = dimmer.state1;
    decltype(dimmer.value1) &lightValue = dimmer.value1;
    decltype(dimmer.setpoint1) &lightSetpoint = dimmer.setpoint1;

    decltype(dimmer.state2) &fanState = dimmer.state2;
    decltype(dimmer.value2) &fanValue = dimmer.value2;
    decltype(dimmer.setpoint2) &fanSetpoint = dimmer.setpoint2;

    // set circuit gain (by resistance)
    void setGain(dtypes::uint32 _ohm)
    {
        dtypes::uint16 _steps;
        dtypes::uint16 maxSteps = maxGainSteps();
        dtypes::uint32 maxGain = gain.base_Ohm.value() + dpotMaxResistance_Ohm();
        // figure out steps for requested gain
        if (gain.base_Ohm.value() > _ohm)
            _steps = 0; // requested gain lower than minimum
        else if (_ohm > maxGain)
            _steps = maxSteps; // requested gain higher than maximum
        else
        {
            _steps = static_cast<dtypes::uint16>(round(static_cast<double>((_ohm - gain.base_Ohm.value())) * maxSteps / dpotMaxResistance_Ohm()));
        }
        setGainSteps(_steps);
    }

    // set circuit gain (by steps, counted in fine dpot1-sized steps)
    void setGainSteps(dtypes::uint16 _steps)
    {
        dtypes::uint16 maxSteps = maxGainSteps();
        if (_steps > maxSteps)
            _steps = maxSteps;

        // figure out the individual digipot steps for the requested gain
        dtypes::uint16 dpot1_steps, dpot2_steps, dpot3_steps;
        if (hasHighGainDpot())
        {
            // >= v2: the coarse high gain 1 MOhm pot (dpot3) is set first (its step is ~10x larger)
            // then the fine 100 kOhm pot (dpot1) trims the remainder.
            // convert the fine-step count into a target resistance
            dtypes::uint32 target_Ohm = static_cast<dtypes::uint32>(round(static_cast<double>(_steps) * dpotMaxResistance_Ohm() / maxSteps));
            // largest dpot3 setting that does not overshoot the target (floor via truncation)
            dtypes::uint32 dpot3_calc = static_cast<dtypes::uint32>(static_cast<double>(target_Ohm) * dpot3.maxSteps / dpot3.maxResistance_Ohm);
            dpot3_steps = (dpot3_calc > dpot3.maxSteps) ? dpot3.maxSteps : static_cast<dtypes::uint16>(dpot3_calc);
            dtypes::uint32 dpot3_Ohm = static_cast<dtypes::uint32>(round(static_cast<double>(dpot3_steps) * dpot3.maxResistance_Ohm / dpot3.maxSteps));
            // fine-tune the remainder with dpot1
            dtypes::uint32 remainder_Ohm = (target_Ohm > dpot3_Ohm) ? (target_Ohm - dpot3_Ohm) : 0;
            dtypes::uint32 dpot1_calc = static_cast<dtypes::uint32>(round(static_cast<double>(remainder_Ohm) * dpot1.maxSteps / dpot1.maxResistance_Ohm));
            dpot1_steps = (dpot1_calc > dpot1.maxSteps) ? dpot1.maxSteps : static_cast<dtypes::uint16>(dpot1_calc);
            dpot2_steps = 0;
        }
        else
        {
            // v1: two equal 100 kOhm pots (dpot1 then dpot2) in series
            if (_steps > dpot1.maxSteps)
            {
                dpot1_steps = dpot1.maxSteps;
                dpot2_steps = _steps - dpot1.maxSteps + 1; // above 0
            }
            else
            {
                dpot1_steps = _steps;
                dpot2_steps = 0;
            }
            dpot3_steps = 0;
        }

        // set steps on dpot1 (always present) via I2C
        dpot1.steps = dpot1_steps;
        dpot1.action = ThardwareI2C::Taction::write;
        // keep both secondary pots in sync in the data model, but only send I2C to the one
        // actually populated on this sensor board (leave the absent one silent)
        dpot2.steps = dpot2_steps;
        dpot3.steps = dpot3_steps;
        if (hasHighGainDpot())
            dpot3.action = ThardwareI2C::Taction::write;
        else
            dpot2.action = ThardwareI2C::Taction::write;

        // reset signal stats
        signal.reset();

        // update error information (only the dpots present on this board are relevant)
        if (dpot1.error != Ti2cError::none && gain.error != dpot1.error)
            gain.error = dpot1.error;
        else if (!hasHighGainDpot() && dpot2.error != Ti2cError::none && gain.error != dpot2.error)
            gain.error = dpot2.error;
        else if (hasHighGainDpot() && dpot3.error != Ti2cError::none && gain.error != dpot3.error)
            gain.error = dpot3.error;
        else if (gain.error != Ti2cError::none)
            gain.error = Ti2cError::none;

        // update steps and total gain
        if (gain.error != Ti2cError::none)
        {
            // assign same value to trigger update
            gain.total_Ohm = gain.total_Ohm.value();
        }
        else
        {
            // no error
            if (gain.steps != _steps)
                gain.steps = _steps;
            gain.total_Ohm = gain.base_Ohm.value() + dpot1.resistance_Ohm + (hasHighGainDpot() ? dpot3.resistance_Ohm : dpot2.resistance_Ohm);
        }
    }

    // set beam
    void setBeam(enums::ToffOn::e _state)
    {
        if (_state == enums::ToffOn::off && beamValue != TbeamValue::OFF)
        {
            // beam off
            beamState = TbeamState::OUTPUT_OFF;
            beamAction = Ti2cAction::write;
        }
        else if (_state == enums::ToffOn::on && beamValue != TbeamValue::ON)
        {
            // beam on
            beamState = TbeamState::OUTPUT_ON;
            beamAction = Ti2cAction::write;
        }
    }

    // set light by percentage
    void setLight(enums::ToffOn::e _state, uint8_t _percent = 100)
    {
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

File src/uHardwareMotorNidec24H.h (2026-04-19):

#pragma once

#include "uTypedef.h"
#include "uRunningStats.h"
#include "stats.h"
#include "enums.h"
#include "Particle.h"

// stirrer motor
class ThardwareMotorNidec24H : public TmenuHandle
{

private:
    // initialized
    bool Finitalized = false;

    // speed
    dtypes::uint8 FspeedPin;                  // PWM output pin
    const dtypes::uint16 FspeedFreq = 25000L; // PWM frequency
    Ttimer FspeedCheckTimer;
    Ttimer FspeedUpdateTimer;

    // decoder for speed measurement
    dtypes::uint8 FdecoderPin; // digital pin on decoder
    TisrEvent decoderISR;
    dtypes::TtickCount FdecoderStart = 0L; // when was the decoder last set
    dtypes::uint32 FdecoderCounter = 0L;

    // decoder interrupt
    void decoderChangeISR()
    {
        decoderISR.signal();
    };

    // speed readings/stats
    bool Fstabilized = false;
    dtypes::float32 FcurrentMax = 0;
    TrunningStats FspeedRunningStats;
    TexactHistogram<0, 5000> Fhistogram;

    // step limits (will be refined based on the max and min RPM sdds variables later)
    dtypes::uint16 FminStep = 0;
    dtypes::uint16 FmaxStep = 4095;

    // step to rpm calibration
    struct Calibration
    {
        dtypes::uint16 stepMin; // inclusive
        dtypes::uint16 stepMax; // exclusive (except last)
        dtypes::float32 rpmMin; // inclusive
        dtypes::float32 rpmMax; // inclusive for last
        dtypes::float32 b;      // intercept_mean  (steps at RPM=0 for this calibration)
        dtypes::float32 m;      // slope_mean      (steps per RPM)
    };

    // calibration data
    static constexpr Calibration calibrations[4] = {
        // stepMin stepMax   rpmMin   rpmMax    b(intercept)   m(slope)
        {0, 1000, 236.0f, 1352.0f, 111.0f, 0.693f},
        {1000, 2000, 1335.0f, 2846.0f, 118.0f, 0.693f},
        {2000, 3000, 2812.0f, 4307.0f, 75.9f, 0.702f},
        {3000, 4000, 4263.0f, 5415.0f, 123.0f, 0.691f},
    };
    // average slope
    static constexpr dtypes::float32 Fmavg = (0.693f + 0.693f + 0.702f + 0.691f) / 4.0f;

    // convert rm to step
    dtypes::uint16 rpmToStep(dtypes::uint16 _rpm, bool _checkLimits = true)
    {
        // deal with limits
        if (_checkLimits && _rpm <= minSpeed_rpm)
            return FminStep;
        if (_checkLimits && _rpm >= maxSpeed_rpm)
            return FmaxStep;
        // find calibration
        dtypes::float32 rpm = static_cast<dtypes::float32>(_rpm);
        dtypes::uint8 calib_idx = 0;
        for (; calib_idx < 4; calib_idx++)
        {
            if (rpm <= calibrations[calib_idx].rpmMax)
                break;
        }
        // apply calibration
        return static_cast<dtypes::uint16>(round(calibrations[calib_idx].b + calibrations[calib_idx].m * rpm));
    }

    // convert steps to rpm
    dtypes::uint16 stepToRpm(dtypes::uint16 _step)
    {
        // deal with limits
        if (_step <= FminStep)
            return minSpeed_rpm;
        if (_step >= FmaxStep)
            return maxSpeed_rpm;
        // find calibration
        dtypes::uint8 calib_idx = 0;
        for (; calib_idx < 4; calib_idx++)
        {
            if (_step <= calibrations[calib_idx].stepMax)
                break;
        }
        // apply calibration
        return static_cast<dtypes::uint16>(round((static_cast<dtypes::float32>(_step) - calibrations[calib_idx].b) / calibrations[calib_idx].m));
    }
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

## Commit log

2025-07-16 scad and stl files
    [micrologger_adapter_balch_nozzle_0.4mm.stl, micrologger_adapter_culture60_nozzle_0.4mm.stl, micrologger_adapter_gl45_nozzle_0.4mm.stl, micrologger_adapter_seru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]
2025-07-16 pcb boards
    [controller_board_pcb_v54_schematic_v48.f3d, led_board_pcb_v19_schematic_v7.f3d, sensor_board_pcb_v77_schematic_v52.f3d]
2025-07-17 implement stirrer sdds framework
2025-11-13 kicad files for led board
    [led_board.kicad_pcb, led_board.kicad_sch, led_board_pcb_v19_schematic_v7.f3d]
2025-11-13 update gitignore for pcbs
2025-11-14 controller board in kicad
    [controller_board.kicad_pcb, controller_board.kicad_pcb_bom.csv, controller_board.kicad_sch, controller_board_pcb_v54_schematic_v48.f3d]
2025-11-14 small updates and BOM
    [led_board.kicad_pcb, led_board.kicad_pcb_bom.csv]
2025-11-15 cleanup footprints and symbols
    [controller_board.kicad_pcb_bom.csv, controller_board.kicad_pcb_positions.csv]
2025-11-15 add footprint status to parts
    [controller_board.kicad_pcb_bom.csv, controller_board.kicad_pcb_positions.csv]
2025-11-15 update controller board to version 0.73
    [controller_board.kicad_pcb, controller_board.kicad_pcb_bom.csv, controller_board.kicad_sch]
2025-11-15 update led board to version 0.41
    [led_board.kicad_pcb, led_board.kicad_pcb_bom.csv, led_board.kicad_sch]
2025-11-15 fix label positioning
    [led_board.kicad_pcb]
2025-11-16 fix current for fuse
2025-11-23 fix orientation of text labels
    [led_board.kicad_sch]
2025-12-09 fix size of drill holes for power jack
2025-12-09 add capacitors and I2C level shifter parts
2025-12-09 update controller board to v0.80
    - switch 5V rail to go to device (instead of light output)
    - improve protection of 3V/5V I2C bus by using an IC instead of mosfets
    - bleed resistor from external 5V to gnd to avoid floating voltage
    [controller_board.kicad_pcb, controller_board.kicad_pcb_bom.csv, controller_board.kicad_sch]
2025-12-12 v 0.81 (removed the 5V on the RJ45)
    [controller_board.kicad_pcb, controller_board.kicad_sch]
2025-12-13 include board version information (version 1.0)
    [controller_board.kicad_pcb, controller_board.kicad_pcb_bom.csv, controller_board.kicad_sch]
2025-12-15 update sensor board
    [sensor_board.kicad_pcb, sensor_board.kicad_sch]
2025-12-15 lock controller board parts
    [controller_board.kicad_pcb]
2025-12-15 update part info
    [controller_board.kicad_sch]
2025-12-15 include background for board picture
2025-12-15 update bom list
    [controller_board.kicad_pcb_bom.csv]
2025-12-15 fix red LED part
2025-12-15 sensor board version 1.1
    [sensor_board.kicad_pcb, sensor_board.kicad_pcb_bom.csv, sensor_board.kicad_sch]
2025-12-18 add SDDS controller for Nidec24H motor
2025-12-24 motor test program
2025-12-27 update controller board to version 1.1 - i2c level shifting back to mosfets
    [controller_board.kicad_pcb, controller_board.kicad_pcb_bom.csv, controller_board.kicad_sch, sensor_board.kicad_sch]
2026-01-15 temperature sensor board
    [temperature_board.kicad_pcb, temperature_board.kicad_pcb_bom.csv, temperature_board.kicad_sch]
2026-01-15 add single pin header and temperature sensor chip to footprints/symbols libraru
2026-01-19 introduce reset action for i2c device base class
2026-01-21 implement auto-resume for motor reconnection
2026-01-22 correct units (lower case)
2026-01-23 upgrade to version 1.2
    - lower resistor for indicator LEDs (brighter)
    - better position for indicator LEDs (left/right)
    - io expander beam/indicator LED switched (=backwards compatibility)
    - switch contacts for the fan (opposite to the lights)
    [sensor_board.kicad_pcb, sensor_board.kicad_sch]
2026-01-24 use updated header symbols, otherwise no changes
    [controller_board.kicad_pcb, controller_board.kicad_sch]
2026-01-24 sensor board version 1.3
    [sensor_board.kicad_pcb, sensor_board.kicad_pcb_bom.csv, sensor_board.kicad_sch]
2026-01-24 fix capacitor placaement on sensor board (IN- to SIGNAL)
    [sensor_board.kicad_pcb, sensor_board.kicad_sch]
2026-01-29 add signal stabilizing capacitors to controller and sensor boards
    [controller_board.kicad_pcb, controller_board.kicad_sch, sensor_board.kicad_pcb, sensor_board.kicad_sch]
2026-01-30 update expander to write pin modes before reading values (same as for writing values)
2026-01-30 implement pcb version recognition
2026-01-30 make motor hardware class more specific
2026-01-30 make sure pin definitions happen in the hardware (caused issues with motor)
2026-02-02 add temperature sensor in environment component
2026-02-02 add code for input voltage sensing
2026-02-02 add voltage and temperature reporting
2026-02-03 have sensor be active/passive options
2026-02-05 sensor board version 1.4
    [sensor_board.kicad_pcb, sensor_board.kicad_pcb_bom.csv, sensor_board.kicad_sch]
2026-02-05 controller board version 1.2 (just the signal cap added)
    [controller_board.kicad_pcb, controller_board.kicad_pcb_bom.csv]
2026-02-05 update led board to version 1.0 (just text upates)
    [led_board.kicad_pcb, led_board.kicad_pcb_bom.csv, led_board.kicad_sch]
2026-02-05 version 1.0 of the temperature sensor
    [temperature_board.kicad_pcb]
2026-02-06 make sure sensor state resumes last and fix bug in optical density reading at low stir rates
2026-02-06 save all motor settings
2026-02-06 switch temperature read interval to ms (although with I2C it probably can't go faster than 500ms)
2026-02-25 add dependencies for stl models
    [screws.scad, utils.scad]
2026-02-25 cleanup stl generation code
    [micrologger_controller.scad, micrologger_device.scad]
2026-02-28 make base adapter notches longer and cleanup code
    [micrologger_device.scad]
2026-02-28 add adpater for hungate tube
    [micrologger_device.scad]
2026-02-28 add new stl models
    [micrologger_adapter_hungate_nozzle_0.4mm.stl, micrologger_base_adapter_culture60_nozzle_0.4mm.stl]
2026-02-28 add pngs for stl models
    [png_converter.scad]
2026-02-28 update 3D printed pngs
    [micrologger_base_bottle_adapter_nozzle_0.4mm.stl]
2026-03-02 make base adapter hooks longer
    [micrologger_base_bottle_adapter_nozzle_0.4mm.stl, micrologger_device.scad]
2026-03-06 optimize printing for fewer travels (with 8 wall print)
    [micrologger_device.scad, micrologger_device_nozzle_0.4mm.stl]
2026-03-06 make base adapters screw attachable
    [micrologger_base_adapter_culture60_nozzle_0.4mm.stl, micrologger_base_bottle_adapter_nozzle_0.4mm.stl, micrologger_device.scad]
2026-04-20 clarify controller is designed for 0.5mm nozzle
    [micrologger_controller.scad]
2026-04-20 add custom prints and increase beam block depth to 7.5mm to accomodate a wider range of LEDs
    [micrologger_device.scad]
2026-05-02 update LED board with multiple resistor options
    [led_board.kicad_pcb, led_board.kicad_sch]
2026-05-02 update LED board with multiple resistors and jumper
    [led_board.kicad_pcb, led_board.kicad_pcb_bom.csv]
2026-05-02 update sensor board with 1M potentiometer
    [sensor_board.kicad_pcb, sensor_board.kicad_pcb_bom.csv, sensor_board.kicad_sch]
